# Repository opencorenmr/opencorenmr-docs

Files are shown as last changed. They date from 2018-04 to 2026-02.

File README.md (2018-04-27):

## Welcome to GitHub Pages

You can use the [editor on GitHub](https://github.com/opencorenmr/opencorenmr.github.io/edit/master/README.md) to maintain and preview the content for your website in Markdown files.

Whenever you commit to this repository, GitHub Pages will run [Jekyll](https://jekyllrb.com/) to rebuild the pages in your site, from the content in your Markdown files.

### Markdown

Markdown is a lightweight and easy-to-use syntax for styling your writing. It includes conventions for

```markdown
Syntax highlighted code block

# Header 1
## Header 2
### Header 3

- Bulleted
- List

1. Numbered
2. List

**Bold** and _Italic_ and `Code` text

[Link](url) and ![Image](src)
```

For more details see [GitHub Flavored Markdown](https://guides.github.com/features/mastering-markdown/).

### Jekyll Themes

Your Pages site will use the layout and styles from the Jekyll theme you have selected in your [repository settings](https://github.com/opencorenmr/opencorenmr.github.io/settings). The name of this theme is saved in the Jekyll `_config.yml` configuration file.

### Support or Contact

Having trouble with Pages? Check out our [documentation](https://help.github.com/categories/github-pages-basics/) or [contact support](https://github.com/contact) and we’ll help you sort it out.

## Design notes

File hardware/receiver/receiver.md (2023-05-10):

# Receiver

11 Mar 2019 Revised by Kazuyuki Takeda
8 Mar 2019 document created by Kazuyuki Takeda

[Back to Home](../../index.md)  

- - -
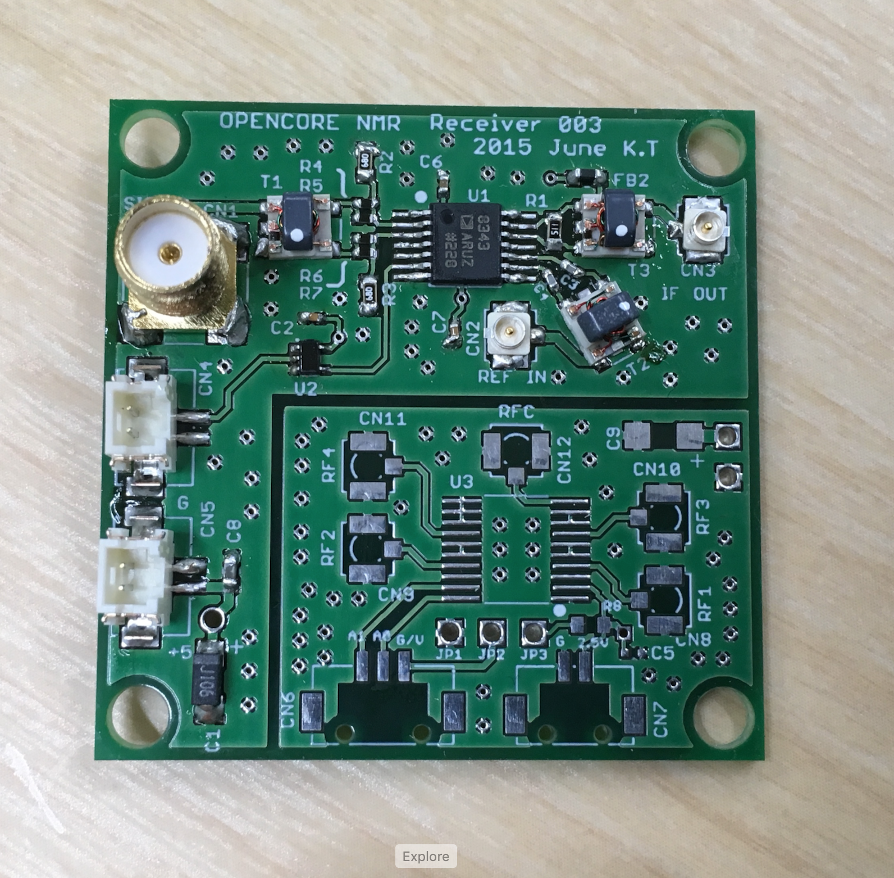
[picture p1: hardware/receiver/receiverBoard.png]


Note that the right bottom part of the board serves for an optional receiver-channel selector. That is, you may leave this part blank, like the one in the photo shown here. In our lab we make fully use of it. How to built/use the channel selector will be described elsewhere.

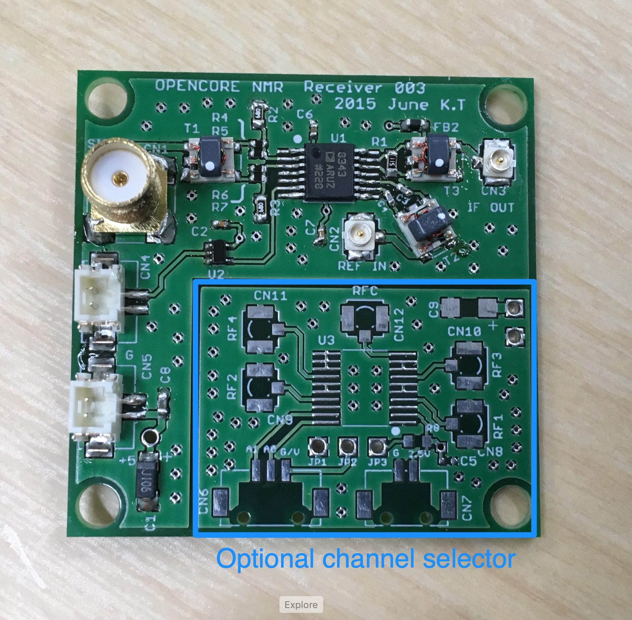
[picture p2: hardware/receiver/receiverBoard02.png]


### Board Design  

- The board was designed on EAGLE 6.2.0 Professional  
- There are **4 layers**. That is, in addition to the top and bottom layers, the board has two inner layers.  

##### EAGLE schematic and board files
- Schematic: [rcvr003.sch](data/rcvr003.sch)  
- Board: [rcvr003.brd](data/rcvr003.brd)  

##### Gerber files

- [rcvr003.cmp](data/gerber/rcvr003.cmp) (Component side pattern)
- [rcvr003.plc](data/gerber/rcvr003.plc)（Component side silkscreen)
- [rcvr003.sol](data/gerber/rcvr003.sol)（Solder side pattern）
- [rcvr003.stc](data/gerber/rcvr003.stc)（Component side solder resist）
- [rcvr003.sts](data/gerber/rcvr003.sts)（Solder side solder resist）
- [rcvr003.2l](data/gerber/rcvr003.2l)（2nd (inner) layer pattern）
- [rcvr003.3l](data/gerber/rcvr003.3l)（3rd (inner) layer pattern）
- [rcvr003.out](data/gerber/rcvr003.out)（outline）
- [rcvr003.dri](data/gerber/rcvr003.dri) (drill list）
- [rcvr003.drd](data/gerber/rcvr003.drd)（drill data）

**Note**: The *component side* mean the top (1st) layer, while the *solder side* does the bottom layer.

##### Component layer
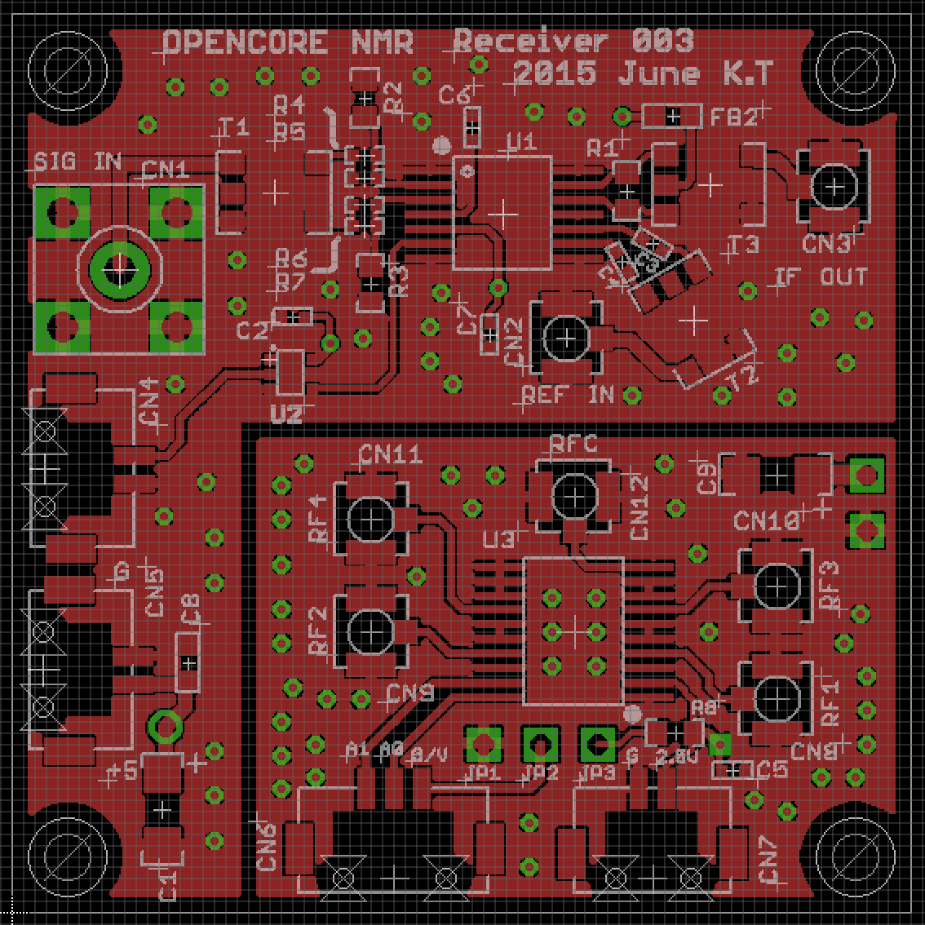
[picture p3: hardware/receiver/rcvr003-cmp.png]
  

##### 2nd (inner) layer
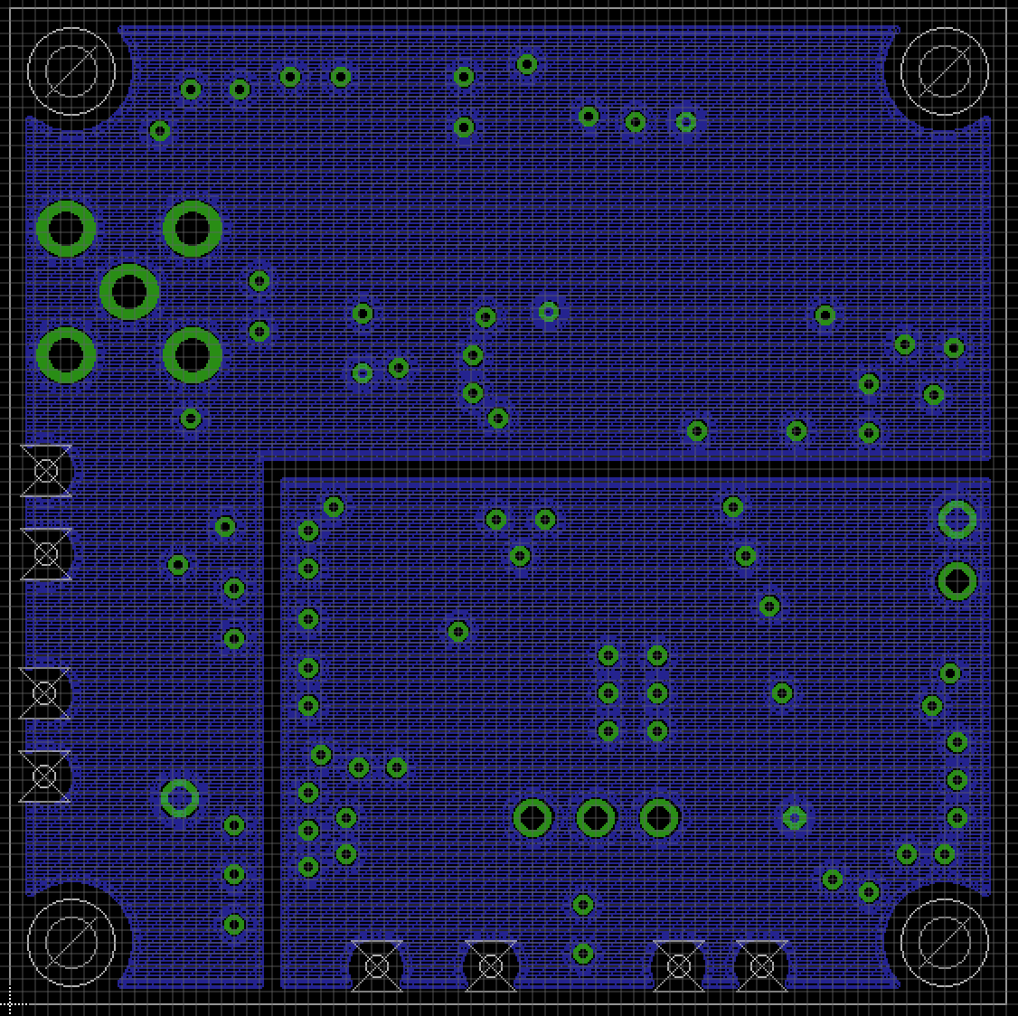
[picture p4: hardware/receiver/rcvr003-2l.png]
  

##### 3rd (inner) layer
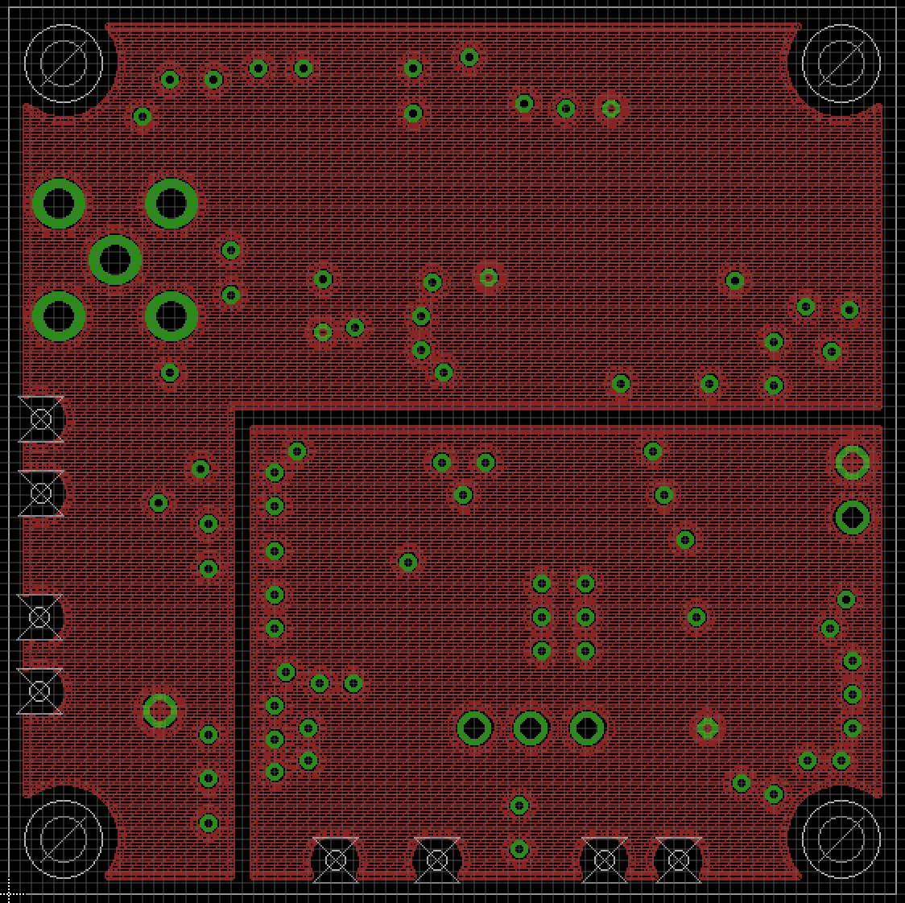
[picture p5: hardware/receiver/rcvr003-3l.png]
  

##### Bottom layer
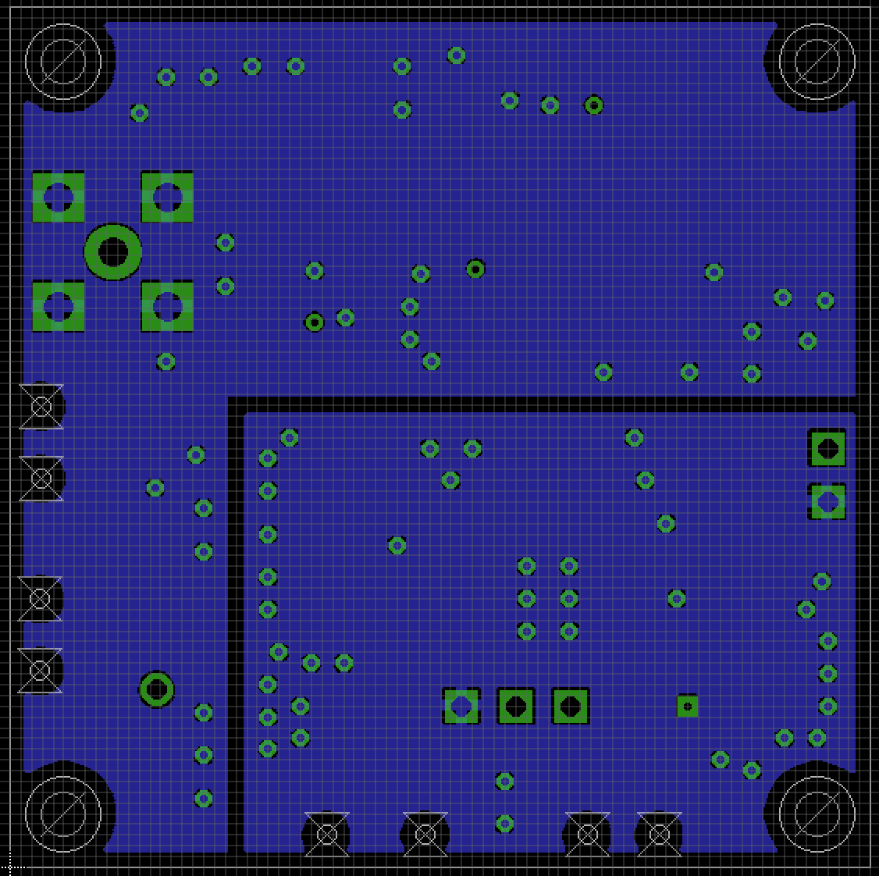
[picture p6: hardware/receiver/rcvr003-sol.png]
  

### Parts List

Part| 	Value | 	Device | 	Package	| Description
---|---|---|---|---
C1  | 10u	  | Tantalum Capacitor |3216 (polar) 	|
C2  | 0.01u	| Capacitor	| 1005	|
C3  | 0.1u	| Capacitor	| 1005	|
C4  | 0.1u	| Capacitor	| 1005	|
C5  | 0.1u	| Capacitor	| 1005	|
C6  | 0.1u	| Capacitor	| 1005	|
C7  | 0.01u	| Capacitor	| 1005	|
C8  | 0.01u	| Capacitor	| 1608	|
C9  | 10u	  | Tantalum Capacitor | 3216 (polar)	|
CN1 | |  SMA Straight PCB Socket | | 5-1814832-1 (TE Connectivity)
CN2 | |  U.FL-R-SMT |		| HIROSE
CN3 | |  U.FL-R-SMT | 	| HIROSE
CN4 | |  DF13-2P-1.25V	| 1.25mm Pitch Miniature Crimping Connector | HIROSE
CN5 | |  DF13-2P-1.25V	| 1.25mm Pitch Miniature Crimping Connector | HIROSE		
CN6 | |  DF13-3P-1.25V	| 1.25mm Pitch Miniature Crimping Connector | HIROSE		
CN7 | |  DF13-2P-1.25V	| 1.25mm Pitch Miniature Crimping Connector | HIROSE		
CN8 | |  U.FL-R-SMT |		| HIROSE
CN9 | |  U.FL-R-SMT |		| HIROSE
CN10|	|  U.FL-R-SMT |		| HIROSE
CN11|	|  U.FL-R-SMT |		| HIROSE
CN12|	|  U.FL-R-SMT |		| HIROSE
FB2  |  30 Ohm @ 100 MHz   |  MPZ1608S300A   | 1608   | Ferrite bead (TDK)    
R1  |	  510 | Resistor	| 1608
R2  |	  68  | Resistor	| 1608
R3  |	  68  | Resistor	| 1608
R4  |	  10  | Resistor	| 1005
R5  |	  10  | Resistor	| 1005
R6  |	  10  | Resistor	| 1005
R7  |	  10  | Resistor	| 1005
R8  |	  100 |  Resistor	| 1608
T1  |	  | TC4-1W+	   |  AT224	| RF transformer (Mini Circuits)
T2  |	  | TC1-1-13M+ | 	AT224	| RF transformer (Mini Circuits)
T3  |	  | TC4-1W+    | 	AT224	| RF transformer (Mini Circuits)
U1  |	  | AD8343     | 		
U2  |	  | MC74VHC1G04| 	 | Logic Inverter
U3  |	  | ADG904     | 	TSSOP

- - -
[Back to Top](../../index.md)

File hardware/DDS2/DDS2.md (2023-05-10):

# DDS2

9 Mar 2019 Revised by Kazuyuki Takeda
2 Mar 2019 Kazuyuki Takeda

[Back to Home](../../index.md)  
- - -

This board serves for a direct digital synthesizer (DDS). Each rf channel of the Opencore NMR spectrometer is equipped with two separate DDS. The first DDS is implemented on the [mother board](../motherBoard/motherMoard.md). Here, we described the *second* one, which we call DDS2.
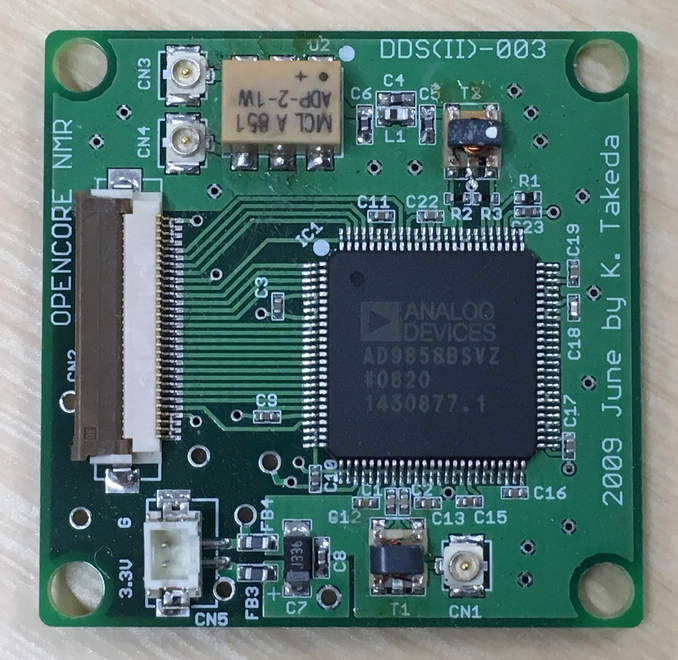
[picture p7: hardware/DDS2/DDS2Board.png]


- - -

### Board design

- The board was designed on EAGLE 6.2.0 Professional  
- There are **4 layers**. That is, in addition to the top and bottom layers, the board has two inner layers.  

##### EAGLE schematic and board files
- Schematic: [DDS2-03.sch](data/DDS2-03.sch)  
- Board: [DDS2-03.brd](data/DDS2-03.brd)  

##### Gerber files
- [DDS2-03.cmp](data/gerber/DDS2-03.cmp)  (Component side pattern)
- [DDS2-03.plc](data/gerber/DDS2-03.plc)  (Component side silkscreen)
- [DDS2-03.sol](data/gerber/DDS2-03.sol)  (Solder side pattern)
- [DDS2-03.stc](data/gerber/DDS2-03.stc)  (Component side solder resist)
- [DDS2-03.sts](data/gerber/DDS2-03.sts)  (Solder side solder resist)
- [DDS2-03.pls](data/gerber/DDS2-03.pls)  (Solder side silkscreen)
- [DDS2-03.2l ](data/gerber/DDS2-03.2l )  (2nd (inner) layer pattern)
- [DDS2-03.3l ](data/gerber/DDS2-03.3l )  (3rd (inner) layer pattern)
- [DDS2-03.out](data/gerber/DDS2-03.out)  (outline)
- [DDS2-03.dri](data/gerber/DDS2-03.dri)  (drill list)
- [DDS2-03.drd](data/gerber/DDS2-03.drd)  (drill data)

**Note**: The *component side* mean the top (1st) layer, while the *solder side* does the bottom layer.

##### Component side (1st layer)
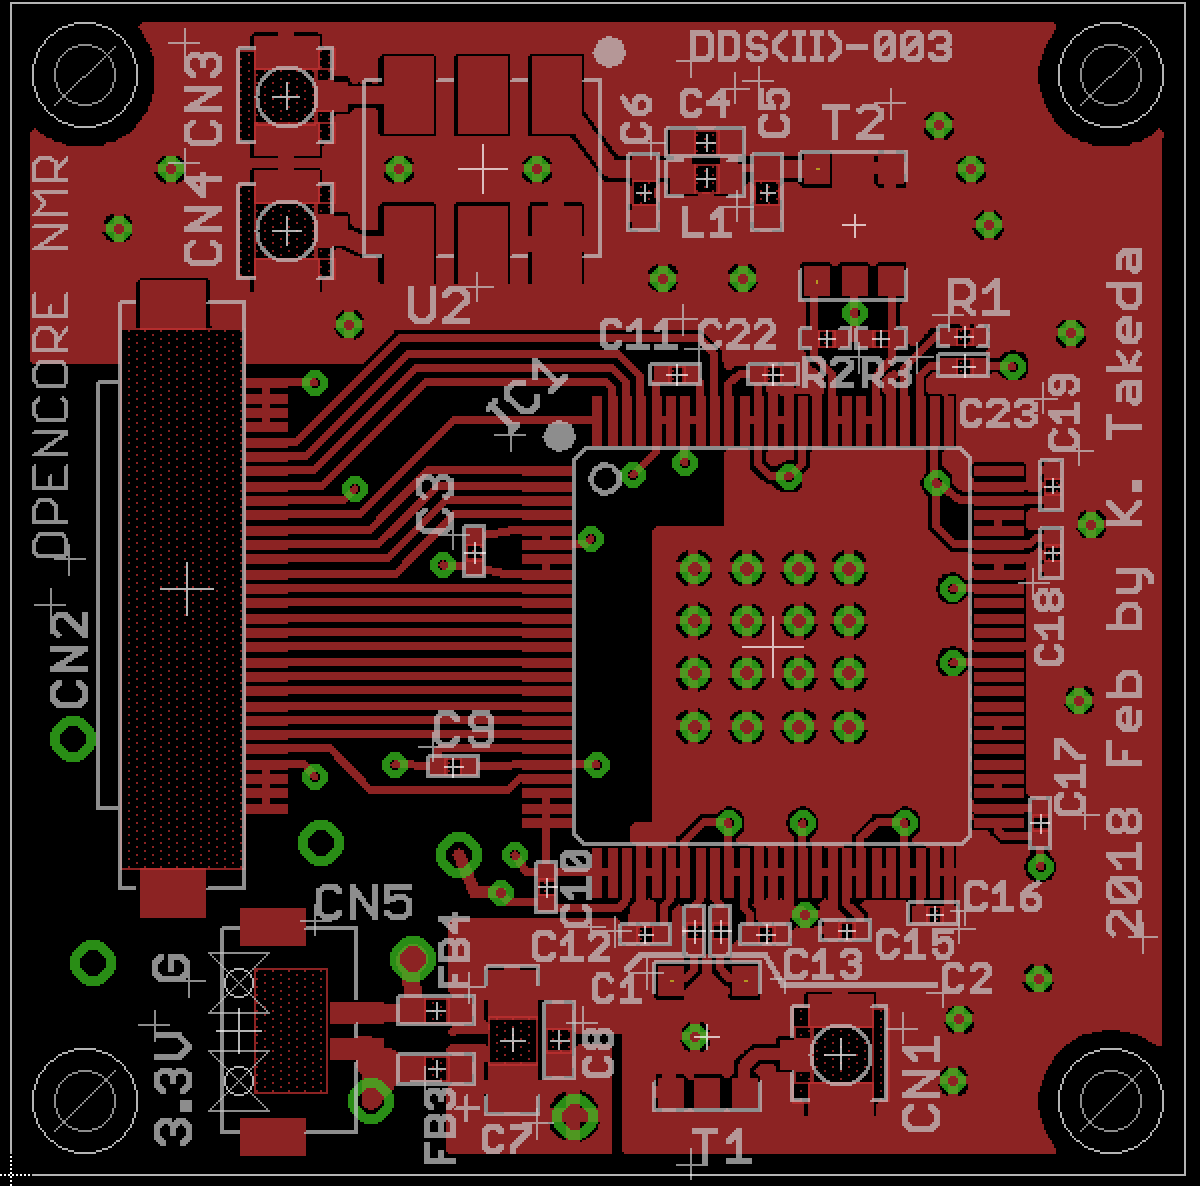
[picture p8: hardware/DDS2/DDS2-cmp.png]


##### 2nd (inner) layer
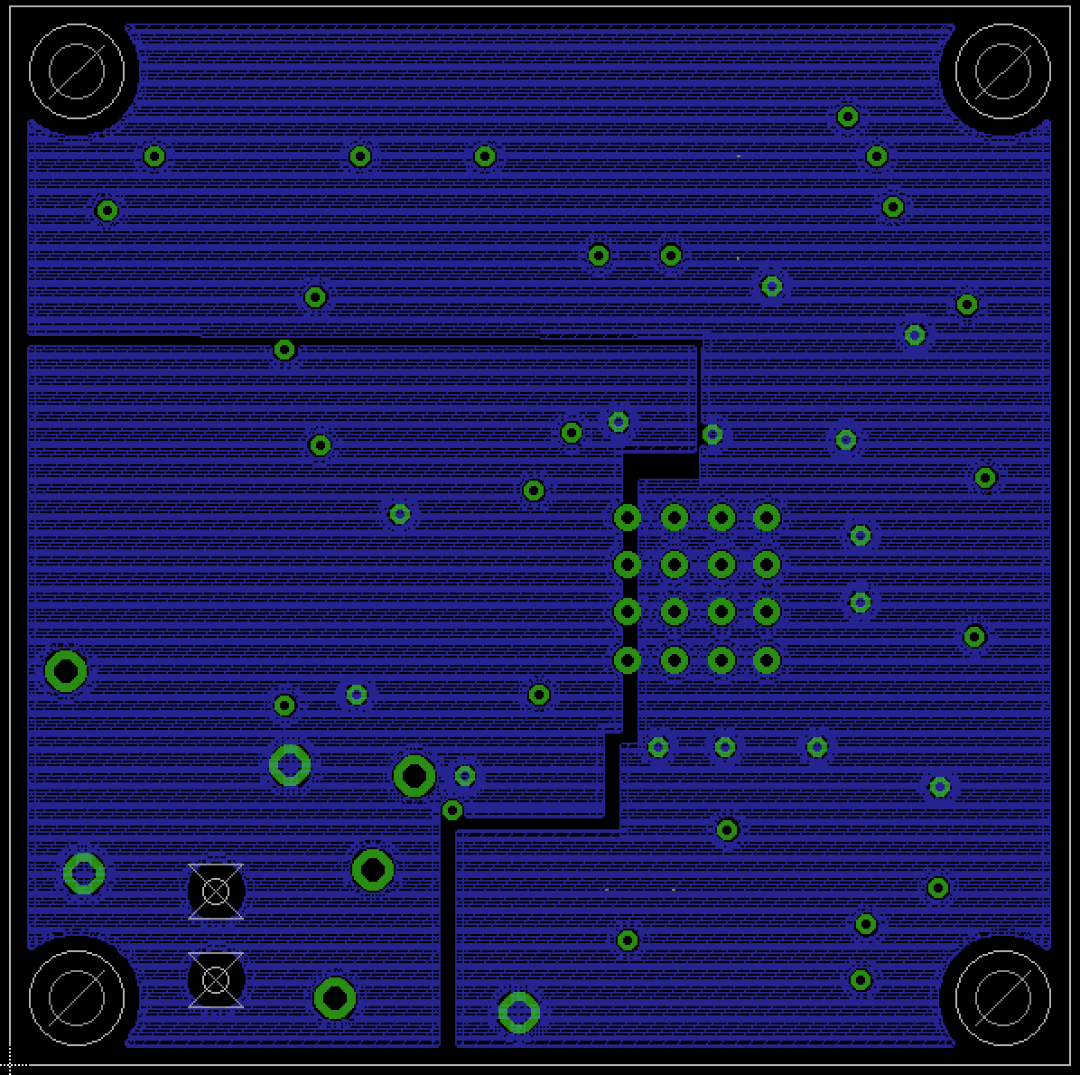
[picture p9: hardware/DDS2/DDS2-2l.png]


##### 3rd (inner) layer
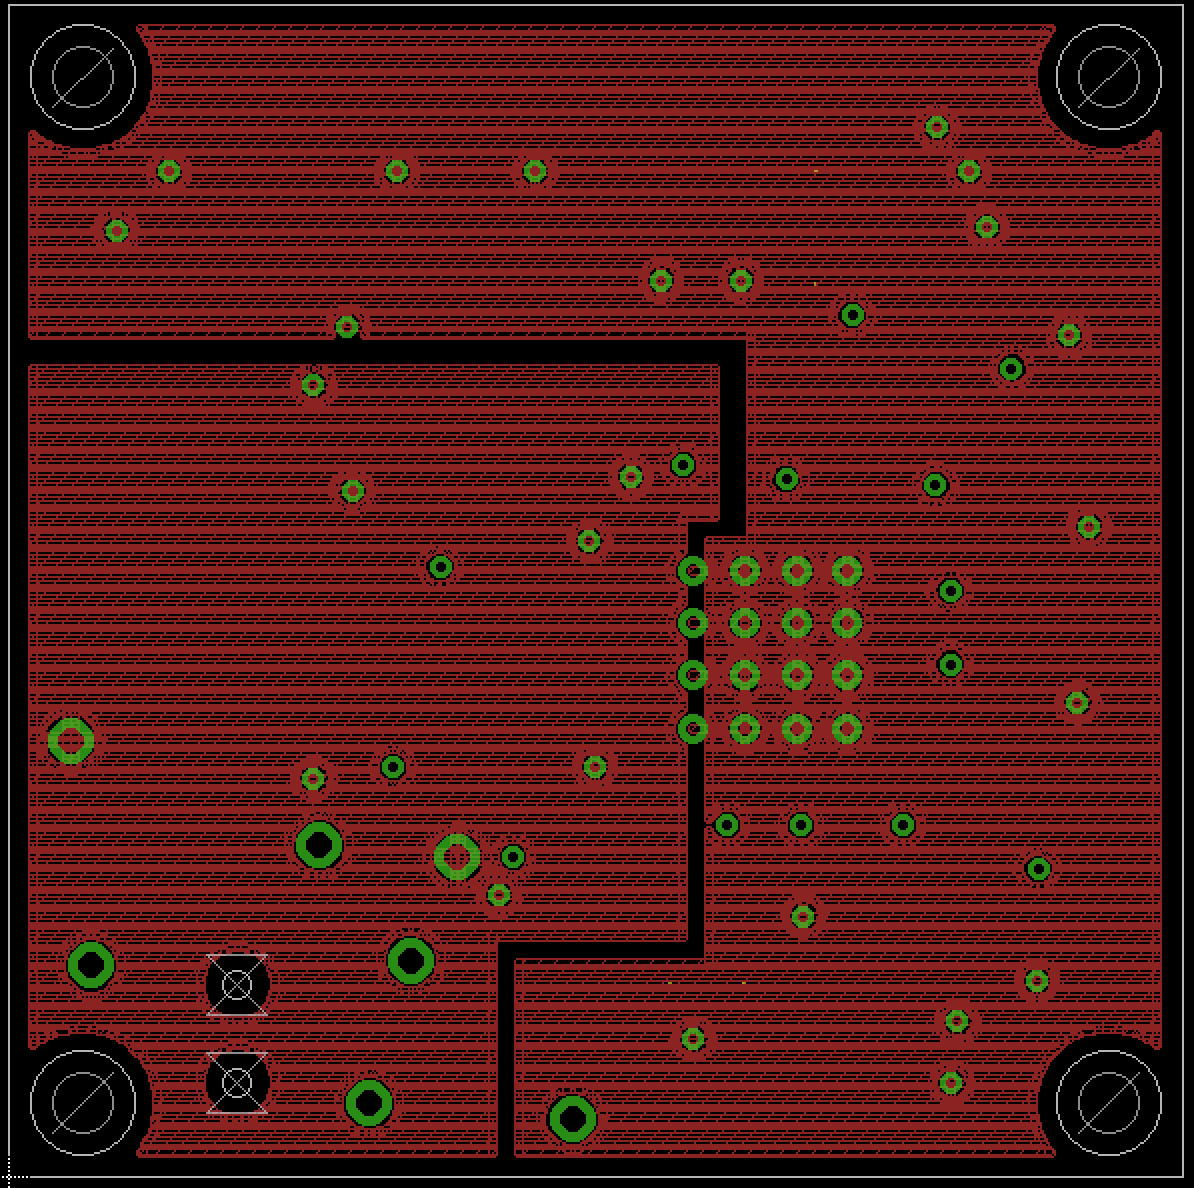
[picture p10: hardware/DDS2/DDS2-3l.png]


##### Solder side (bottom layer)
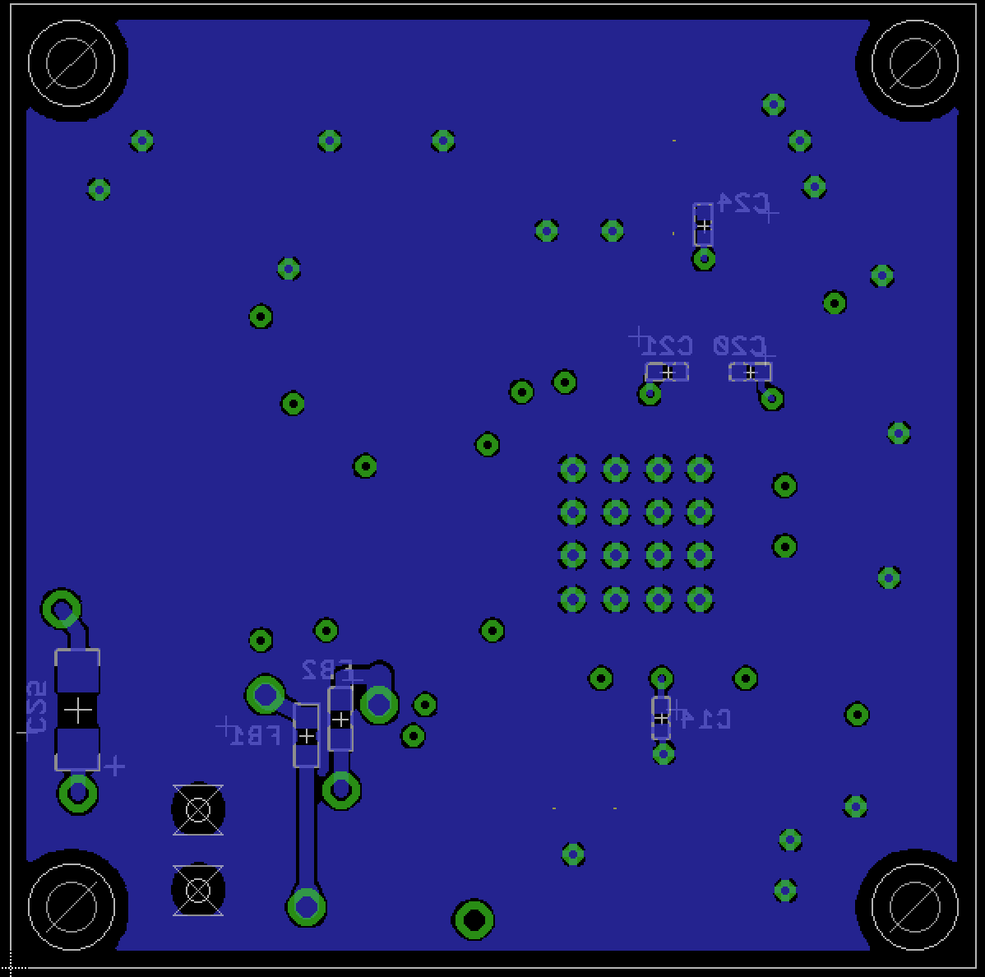
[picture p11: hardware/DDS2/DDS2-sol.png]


### Parts List

Part	| Value | 	Device	| Package | Description
---|---|---|---|---
C1	| 1000p	| C	| 1005
C2	| 1000p	| C	| 1005
C3	| 0.1u	| C	| 1005
C4	| 6p	  | C	| 1608
C5	| 12p	  | C	| 1608
C6	| 12p	  | C	| 1608
C7	| 33u	  | C	| 3216 (polar) | tantalum
C8	| 0.01u	| C	| 1608
C9	| 0.1u	| C	| 1005
C10	| 0.1u	| C	| 1005
C11	| 0.1u	| C	| 1005
C12	| 0.01u	| C	| 1005
C13	| 0.01u	| C	| 1005
C14	| 0.01u	| C	| 1005
C15	| 0.01u	| C	| 1005
C16	| 0.01u	| C	| 1005
C17	| 0.01u	| C	| 1005
C18	| 0.01u	| C	| 1005
C19	| 0.01u	| C	| 1005
C20	| 0.01u	| C	| 1005
C21	| 0.01u	| C	| 1005
C22	| 0.01u	| C	| 1005
C23	| 0.1u	| C	| 1005
C24	| 0.01u	| C	| 1005
C25	| 33u	  | C	| 3216 (polar) | tantalum
CN1	| 	    | U.FL-R-SMT | | (HIROSE)		
CN2	| 	    | FH12-30S-0.5SH | | (HIROSE)		0.5mm pitch FPC connector
CN3	| 	    | U.FL-R-SMT | | (HIROSE)		
CN4	| 	    | U.FL-R-SMT | | (HIROSE)		
CN5	| 	    | DF13-2P-1.25V | | (HIROSE)		
FB1  |  30 Ohm @ 100 MHz   |  MPZ1608S300A   | 1608           | Ferrite bead (TDK)
FB2  |  30 Ohm @ 100 MHz   |  MPZ1608S300A   | 1608           | Ferrite bead (TDK)
FB3  |  30 Ohm @ 100 MHz   |  MPZ1608S300A   | 1608           | Ferrite bead (TDK)
FB4  |  30 Ohm @ 100 MHz   |  MPZ1608S300A   | 1608           | Ferrite bead (TDK)
U1	| 	    | AD9858 | | (Analog Divices)		DDS chip
L1	| 12nH	| L | 1608
R1	| 2k	  | R | 1005
R2	| 27	  | R | 1005
R3	| 27	  | R | 1005
T1	| 	    | TC1-1-13M+ | | (Mini Circuits)	AT224	RF transformer
T2	| 	    | TC1-1T+ |  |(Mini Circuits)	AT224	RF transformer
U2	| 	    | ADP-2-1W | | (Mini Circuits)		RF splitter

- - -
[Back to Home](../../index.md)

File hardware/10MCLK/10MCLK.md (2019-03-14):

# 10 MHz Clock

14 Mar 2019 Kazuyuki Takeda

[Back to Home](../../index.md)  
- - -

This board generates a clock signal at 10 MHz. On the board, the clock signal is fan-out into several ports. The 10 MHz clock signal is required for the [mother board](../motherBoard/motherMoard.md). as well as 1 GHz clock module, to be described in due time.
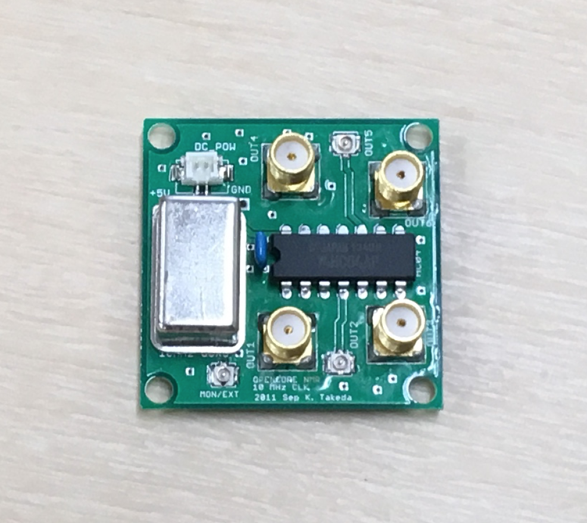
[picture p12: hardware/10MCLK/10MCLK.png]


- - -

### Board design

- The board was designed on EAGLE 6.2.0 Professional  
- There are **2 layers**, the top and the bottom layers.

##### EAGLE schematic and board files
- Board: [10MCLK02.brd](data/10MCLK02.brd)  

##### Gerber files
- [10MCLK02.cmp](data/gerber/10MCLK02.cmp)  (Component side pattern)
- [10MCLK02.plc](data/gerber/10MCLK02.plc)  (Component side silkscreen)
- [10MCLK02.sol](data/gerber/10MCLK02.sol)  (Solder side pattern)
- [10MCLK02.stc](data/gerber/10MCLK02.stc)  (Component side solder resist)
- [10MCLK02.sts](data/gerber/10MCLK02.sts)  (Solder side solder resist)
- [10MCLK02.out](data/gerber/10MCLK02.out)  (outline)
- [10MCLK02.dri](data/gerber/10MCLK02.dri)  (drill list)
- [10MCLK02.drd](data/gerber/10MCLK02.drd)  (drill data)

**Note**: The *component side* mean the top (1st) layer, while the *solder side* does the bottom layer.

##### Component side (1st layer)
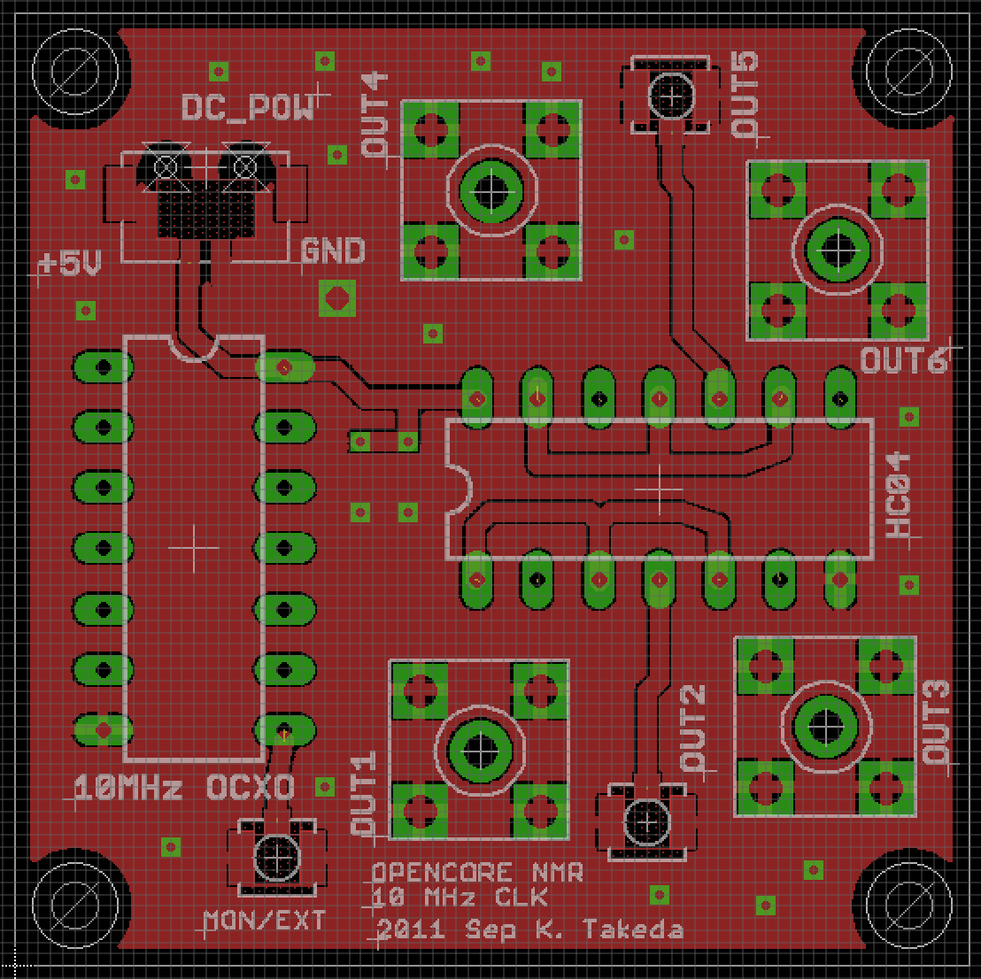
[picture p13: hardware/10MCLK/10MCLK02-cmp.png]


##### Solder side (bottom layer)
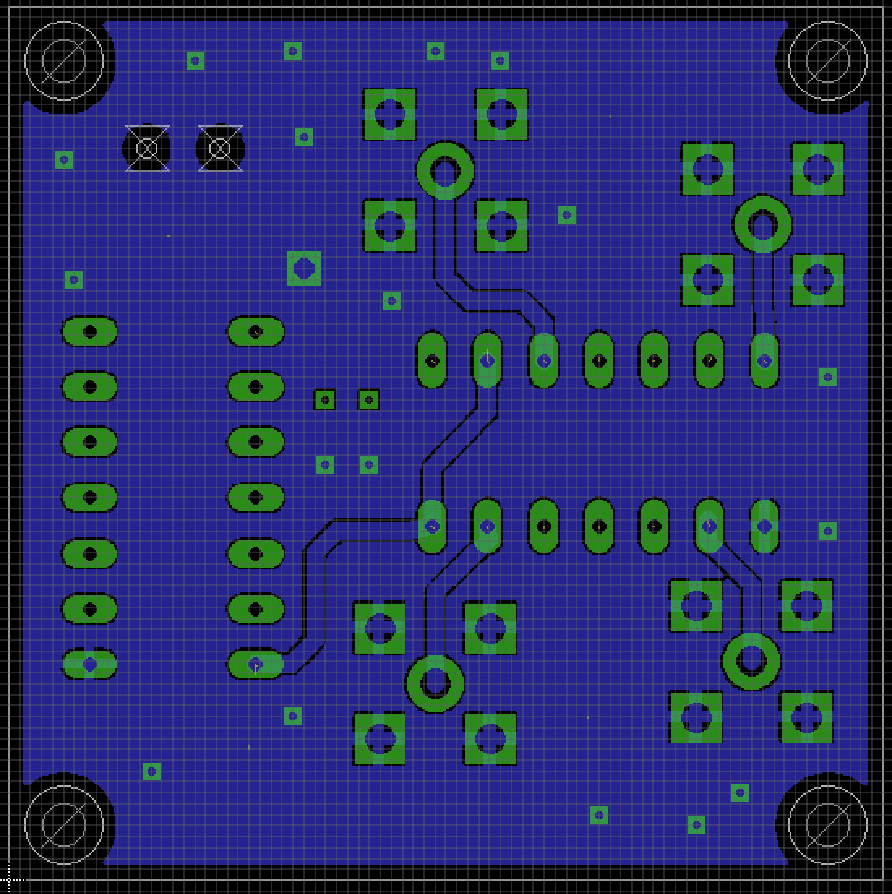
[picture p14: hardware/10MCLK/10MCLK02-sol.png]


### Parts List (TODO)

Part	| Value | 	Device	| Package | Description
---|---|---|---|---
CN	| 	    | U.FL-R-SMT | | (HIROSE)		
CN	| 	    | U.FL-R-SMT | | (HIROSE)		
CN	| 	    | U.FL-R-SMT | | (HIROSE)		

CN	 | 	    | DF13-2P-1.25V | | (HIROSE) 		
CN | |  SMA Straight PCB Socket | | 5-1814832-1 (TE Connectivity)
CN | |  SMA Straight PCB Socket | | 5-1814832-1 (TE Connectivity)
CN | |  SMA Straight PCB Socket | | 5-1814832-1 (TE Connectivity)
CN | |  SMA Straight PCB Socket | | 5-1814832-1 (TE Connectivity)
OCXO   |  | MOFH5200C-10.000 |  | (MMD)
IC  |  | HC04 |
- - -
[Back to Home](../../index.md)

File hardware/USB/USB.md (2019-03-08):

# USB board

5 Mar 2019 Kazuyuki Takeda

[Back to Home](../../index.md)  

- - -
  

This is a 40x40 mm board equipped with FT2232, a dual-line USB driver by [FTDI](https://www.ftdichip.com) inc. This enables apparent simultaneous two-channel data communication between the OPENCORE NMR spectrometer and the console software installed on a personal computer through a single USB cable. In the current architecture of the OPENCORE NMR, the one channel (channel A) is used in the UART 232 mode for sending/receiving the commands/responses to/from the PPG interface core module built inside the FPGA chip, the other (channel B) for transferring the NMR signals from the RCVR core module to the personal computer in the 245 FIFO mode.

Before using, the mode of operation must be configured to the EPROM on the board using the [MProg](https://www.ftdichip.com/Support/Utilities.htm#MProg) software (FTDI).
- [A document on EPROM configuration](https://github.com/opencorenmr/opencorenmr-docs/blob/master/blog/usb_eprom/mprog.md)  

Also, the [D2XX driver](https://www.ftdichip.com/Drivers/D2XX.htm), which is available from FTDI, has to be installed.  

### Board design

- The board was designed on EAGLE 6.2.0 Professional  
- There are **2 layers**, namely, the top (component) and bottom (solder) layers.

##### EAGLE schematic and board files
- Schematic: [USB.sch](data/USB.sch)  
- Board: [USB.brd](data/USB.brd)  

##### Gerber files

- [USB.cmp](data/gerber/USB.cmp) (Component side pattern)
- [USB.plc](data/gerber/USB.plc)（Component side silkscreen)
- [USB.sol](data/gerber/USB.sol)（Solder side pattern）
- [USB.stc](data/gerber/USB.stc)（Component side solder resist）
- [USB.sts](data/gerber/USB.sts)（Solder side solder resist）
- [USB.pls](data/gerber/USB.pls)（Solder side silkscreen）
- [USB.out](data/gerber/USB.out)（outline）
- [USB.dri](data/gerber/USB.dri) (drill list）
- [USB.drd](data/gerber/USB.drd)（drill data）

**Note**: The *component side* mean the top (1st) layer, while the *solder side* does the bottom layer.

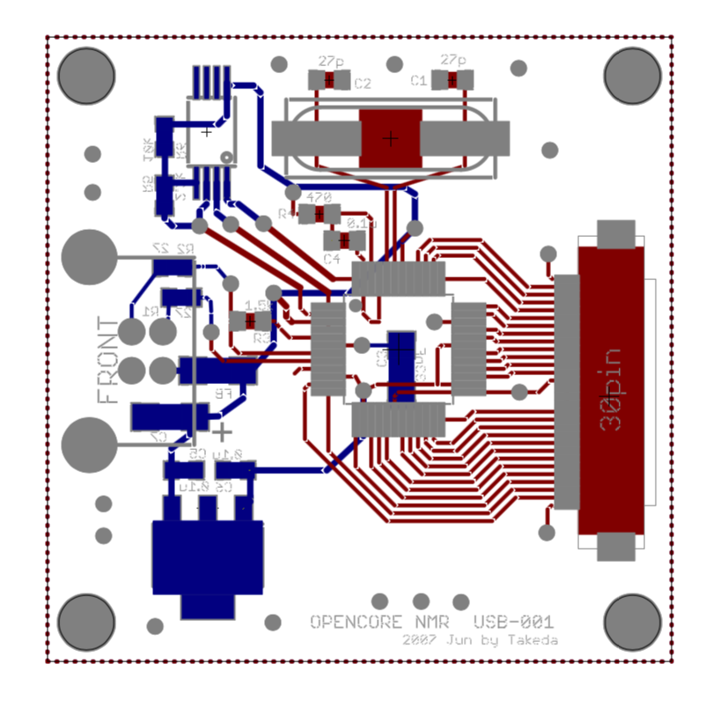
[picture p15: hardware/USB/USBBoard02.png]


### Parts List

Part  | Value  | Device  | Package  | Description
--|---|---|---|--
C1	| *27p | 	C |	1608 |
C2	| *27p | 	C |	1608 |
C3	| 33nF | 	C |	3216 |
C4	| 0.1u | 	C |	1608 |
C5	| 0.1u | 	C |	1608 |
C6	| 0.1u | 	C |	1608 |
C7	| 10u  | 	C |	3216 (polar) | tantalum
CN1	|  | FH12-30S-0.5SH 	| | 	0.5 mm pitch FPC connector (HIROSE)
FB  |  30 Ohm @ 100 MHz   |  MPZ1608S300A   | 1608           | Ferrite bead (TDK)
R1	| 27	  | R	| 1608	|
R2	| 27	  | R	| 1608	|
R3	| 1.5k	| R	| 1608	|
R4	| 470	  | R	| 1608	|
R5	| 2.2k	| R	| 1608	|
R6	| 10k	  | R	| 1608	|
U1	|  | FT2232D	|	| Dual USB UART/FIFO I.C. (FTDI)
U2	|  | 67068-704J  |	|	USB connector (MOLEX)
U3	|  | **AT93C46-10TU-2.7	|  Thin Shrink Small Outline Package (TSSOP) |	Serial EPROM (ATMEL)
U4	|  | LM2937IMP-3.3	| SOT-223	| Voltage regulator
Y1	| 6 MHz	| HC49/4H SMX	| |	6 MHz crystal

*Note: The proper value for C1 and C2 depends on the crystal oscillator. Check the datasheet of the 6 MHz crystal that you use.

**Note: End of production. There should be alternatives. According to the datasheet of FT2232D, EEPROMs with a 16-bit wide configuration are required. And the EEPROM must be operational at a 1 MHz clock rate with a supply voltage between 4.35V and 5.25V.

- - -
[Back to Home](../../index.md)

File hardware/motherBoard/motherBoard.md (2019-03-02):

# Mother board

23 Feb 2019 Kazuyuki Takeda

[Back to Home](../../index.md)  

- - -

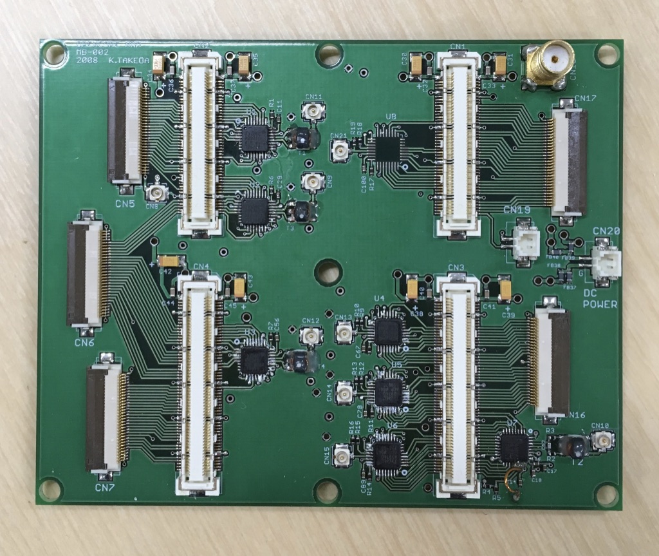
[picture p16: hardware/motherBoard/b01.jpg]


This board, called the *mother board*, is to be docked by either of the following commercial FPGA breadboards:
- [ACM-202-80C8](https://www2.hdl.co.jp/en/altera-series1/cycloneiii/acm-202-ql.html)  (HuMANDATA LTD.)  
- [ACM-206-A7](https://www2.hdl.co.jp/en/altera-series1/cyclonev/acm-206-ql.html) (HuMANDATA LTD.)  



The photo just below shows the *docked* board:
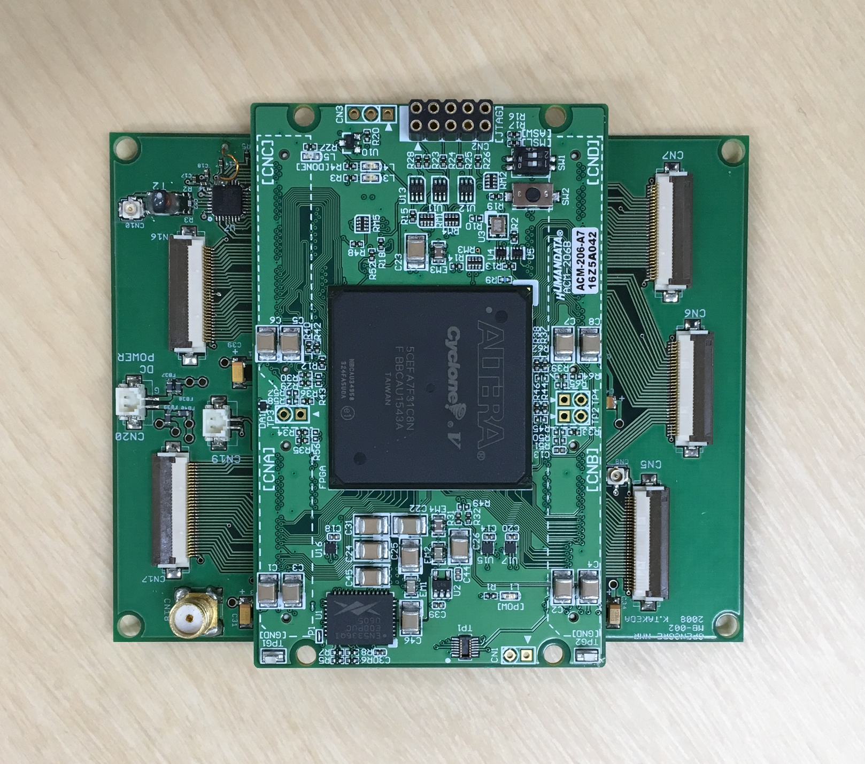
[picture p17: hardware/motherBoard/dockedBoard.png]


- - -

### Board design

- The board was designed on EAGLE 6.2.0 Professional  
- There are **4 layers**. That is, in addition to the top and bottom layers, the board has two inner layers.  

##### EAGLE schematic and board files
- Schematic: [mother-002.sch](data/mother-002.sch)  
- Board: [mother-002.brd](data/mother-002.brd)  

##### Gerber files

- [mother-002.cmp](data/gerber/mother-002.cmp) (Component side pattern)
- [mother-002.plc](data/gerber/mother-002.plc)（Component side silkscreen)
- [mother-002.sol](data/gerber/mother-002.sol)（Solder side pattern）
- [mother-002.stc](data/gerber/mother-002.stc)（Component side solder resist）
- [mother-002.sts](data/gerber/mother-002.sts)（Solder side solder resist）
- [mother-002.pls](data/gerber/mother-002.pls)（Solder side silkscreen）
- [mother-002.2l](data/gerber/mother-002.2l)（2nd (inner) layer pattern）
- [mother-002.3l](data/gerber/mother-002.3l)（3rd (inner) layer pattern）
- [mother-002.out](data/gerber/mother-002.out)（outline）
- [mother-002.dri](data/gerber/mother-002.dri) (drill list）
- [mother-002.drd](data/gerber/mother-002.drd)（drill data）

**Note**: The *component side* mean the top (1st) layer, while the *solder side* does the bottom layer.

##### Component side (1st layer)
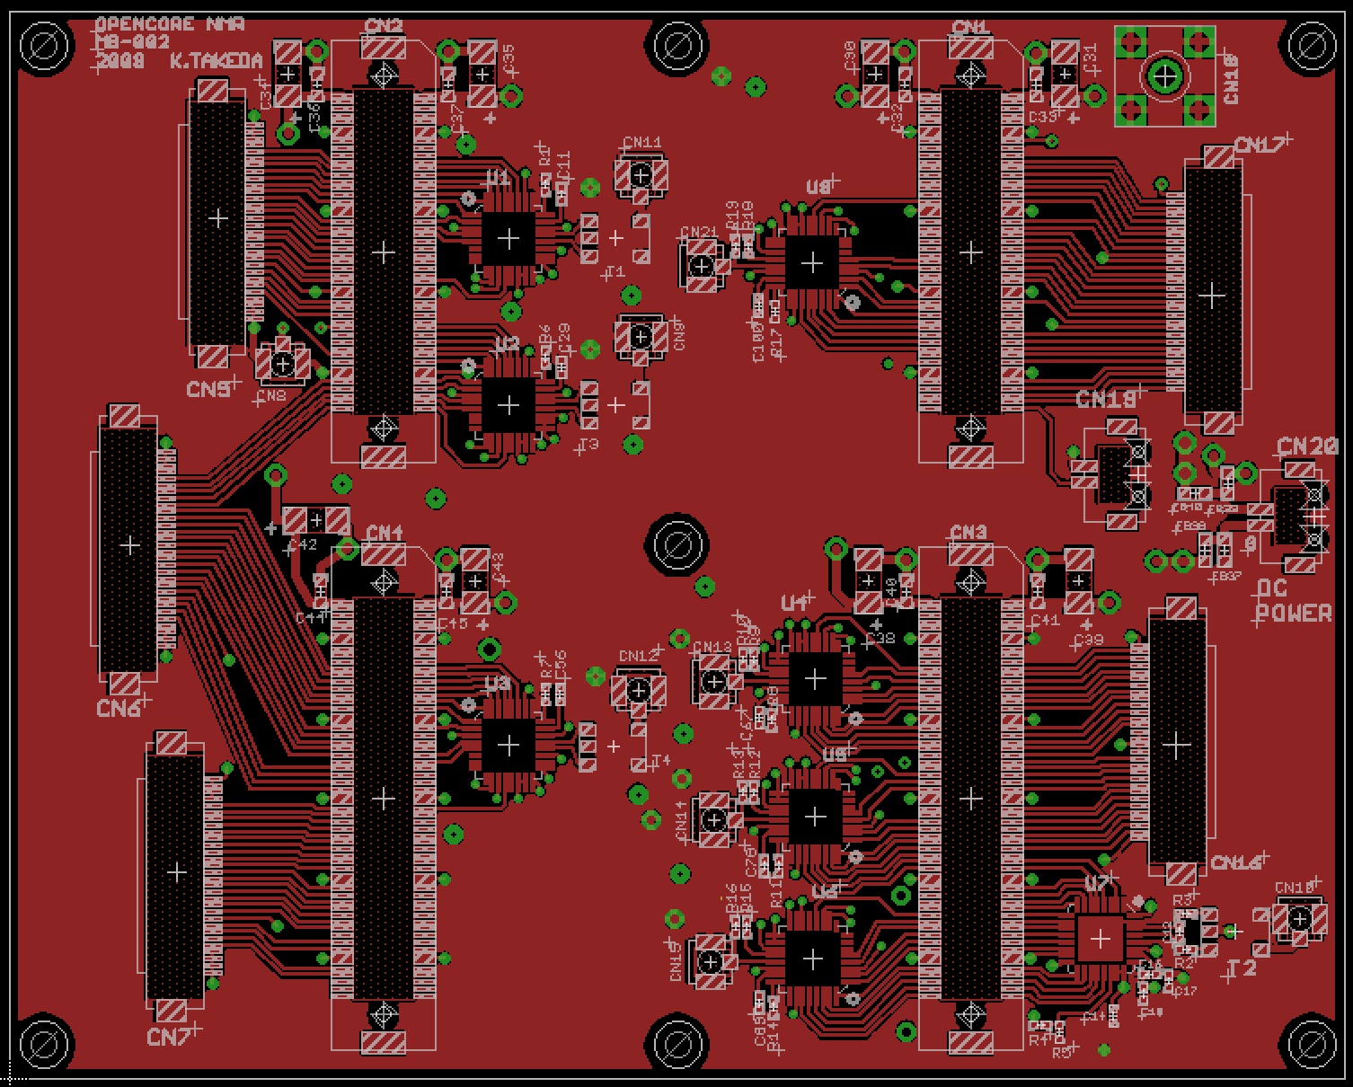
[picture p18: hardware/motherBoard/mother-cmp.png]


##### 2nd (inner) layer
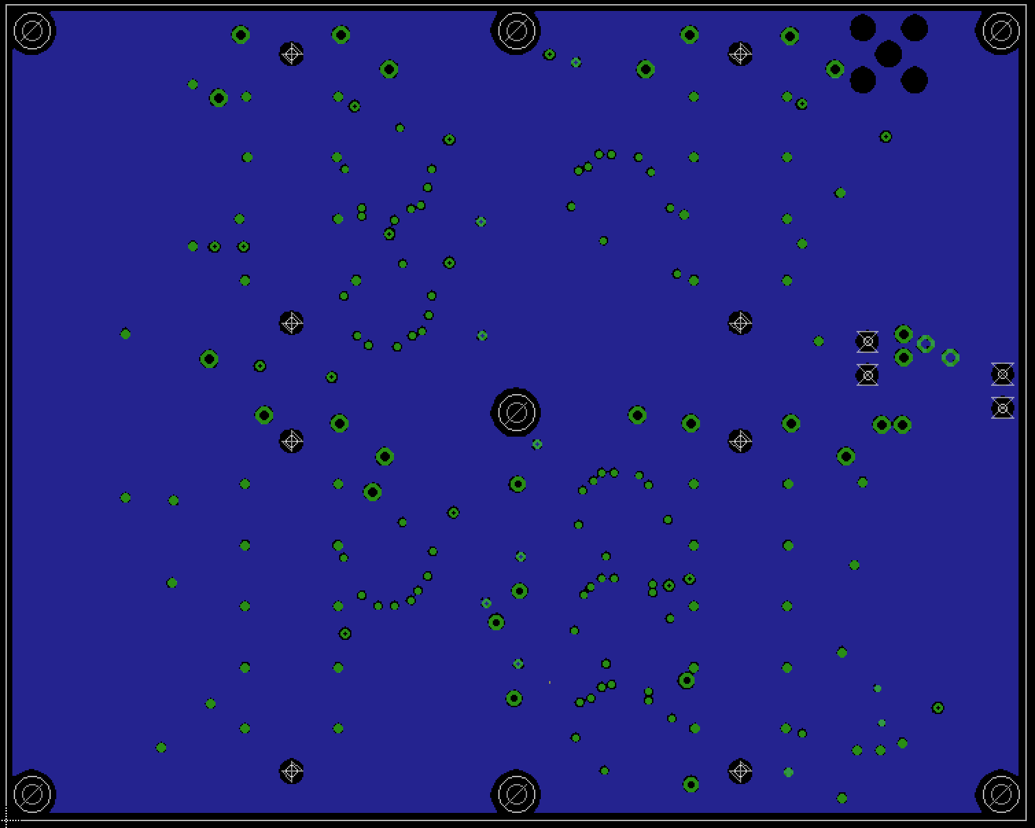
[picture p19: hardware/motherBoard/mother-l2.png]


##### 3rd (inner) layer
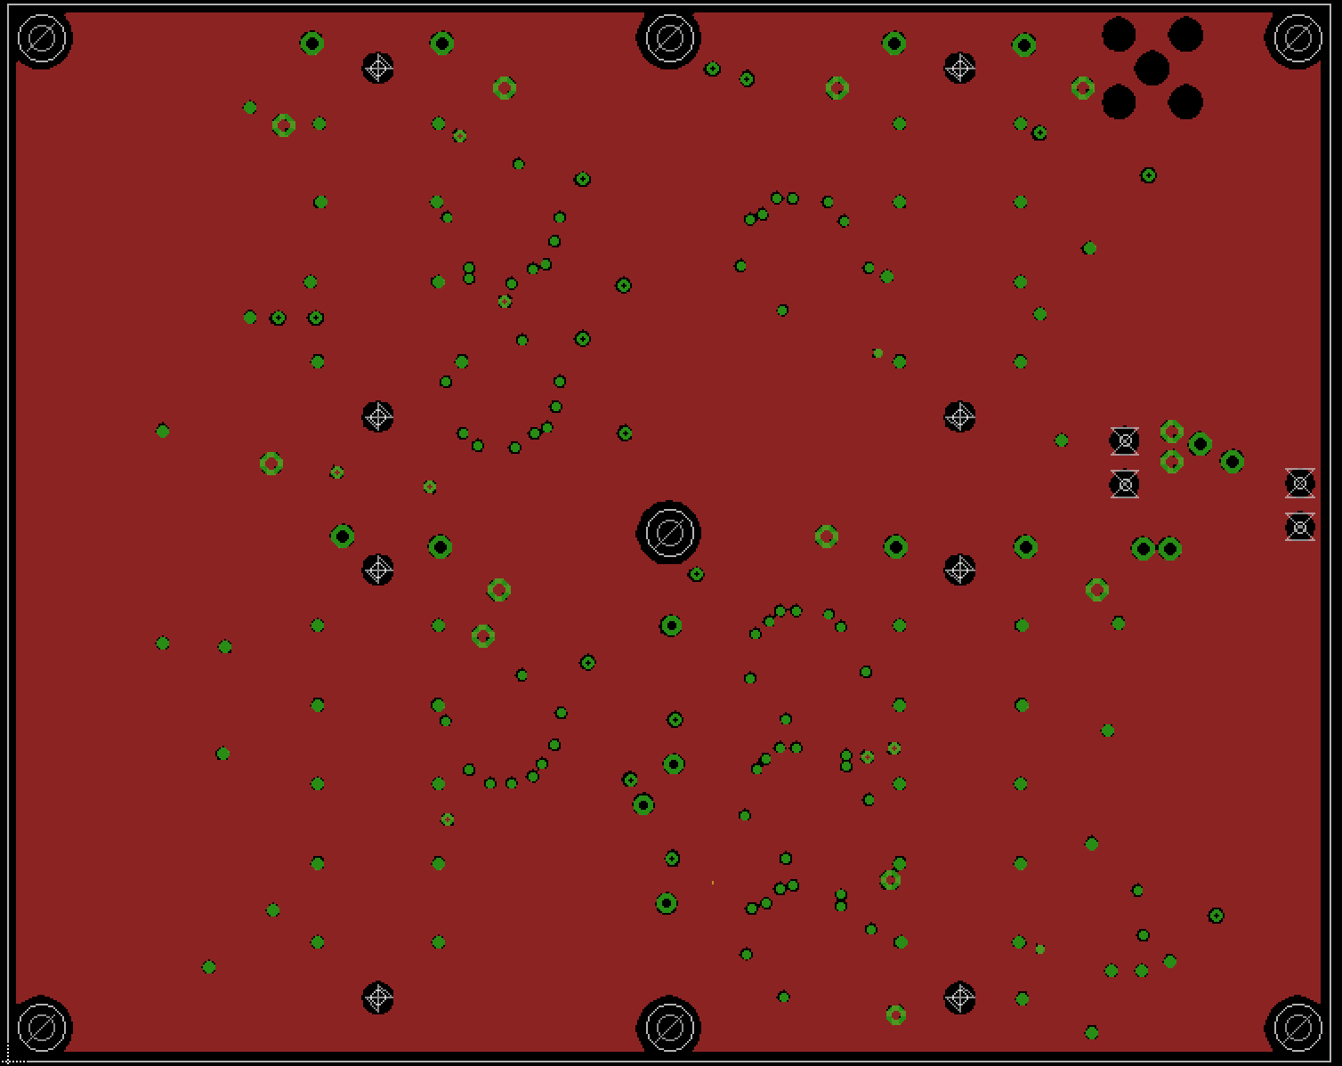
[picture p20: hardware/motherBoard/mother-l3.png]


##### Solder side (bottom layer)
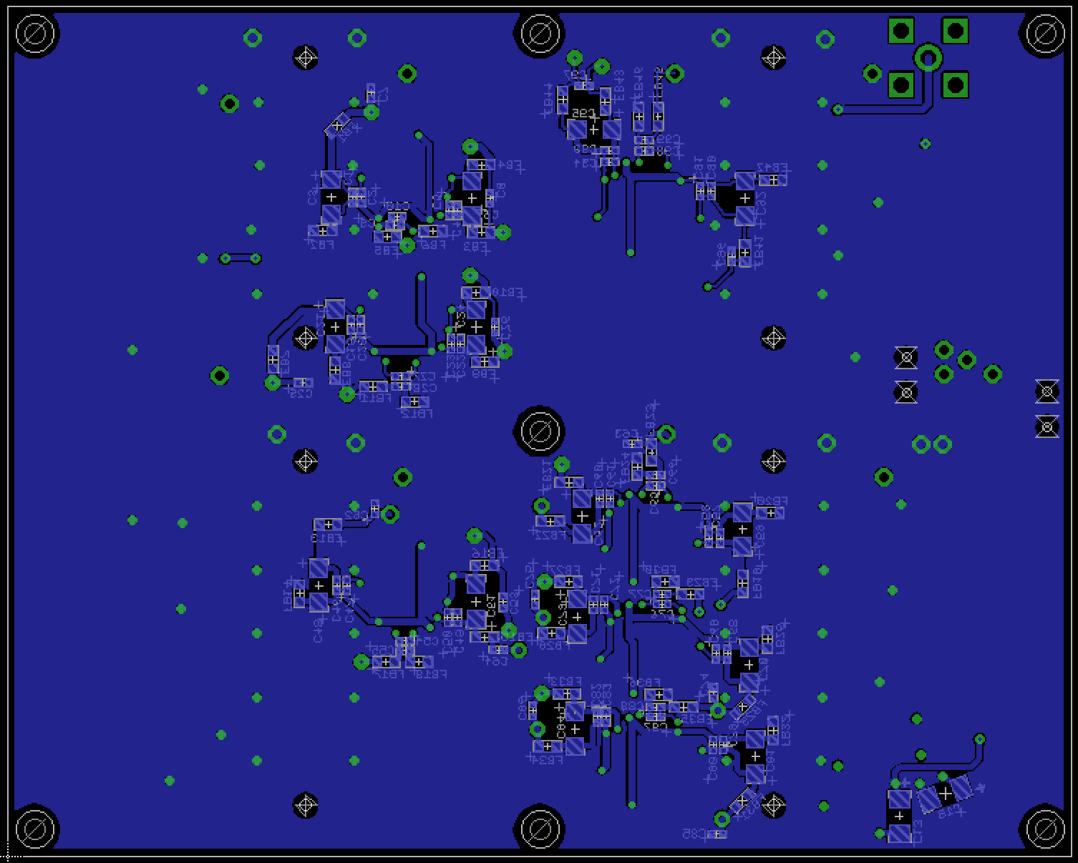
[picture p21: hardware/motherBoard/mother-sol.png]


### Parts List

Part  | Value  | Device  | Package  | Description
--|---|---|---|--
C1   |  0.1u           |  C1005            | 1005           |    
C2   |  1000p          |  C1005            | 1005           |    
C3   |  33u            |  C_POLAR3216      | 3216_POLAR     |    
C4   |  0.1u           |  C1005            | 1005           |    
C5   |  1000p          |  C1005            | 1005           |    
C6   |  33u            |  C_POLAR3216      | 3216_POLAR     |    
C7   |  0.1u           |  C1005            | 1005           |    
C8   |  0.1u           |  C1005            | 1005           |    
C9   |  1000p          |  C1005            | 1005           |    
C10  |  0.1u           |  C1005            | 1005           |    
C11  |  0.1u           |  C1005            | 1005           |    
C12  |  20p            |  C1005            | 1005           |    
C13  |  10uF           |  C_POLAR          | 3216_POLAR     |    
C14  |  0.1uF          |  C1005            | 1005           |    
C15  |  10uF           |  C_POLAR          | 3216_POLAR     |    
C16  |  0.1u           |  C1005            | 1005           |    
C17  |  0.1u           |  C1005            | 1005           |    
C18  |  0.1u           |  C1005            | 1005           |    
C19  |  0.1u           |  C1005            | 1005           |    
C20  |  1000p          |  C1005            | 1005           |    
C21  |  33u            |  C_POLAR3216      | 3216_POLAR     |    
C22  |  0.1u           |  C1005            | 1005           |    
C23  |  1000p          |  C1005            | 1005           |    
C24  |  33u            |  C_POLAR3216      | 3216_POLAR     |    
C25  |  0.1u           |  C1005            | 1005           |    
C26  |  0.1u           |  C1005            | 1005           |    
C27  |  1000p          |  C1005            | 1005           |    
C28  |  0.1u           |  C1005            | 1005           |    
C29  |  0.1u           |  C1005            | 1005           |    
C30  |  33u            |  C_POLAR          | 3216_POLAR     |    
C31  |  33u            |  C_POLAR          | 3216_POLAR     |    
C32  |  0.01u          |  C1608            | 1608           |    
C33  |  0.01u          |  C1608            | 1608           |    
C34  |  33u            |  C_POLAR          | 3216_POLAR     |    
C35  |  33u            |  C_POLAR          | 3216_POLAR     |    
C36  |  0.01u          |  C1608            | 1608           |    
C37  |  0.01u          |  C1608            | 1608           |    
C38  |  33u            |  C_POLAR          | 3216_POLAR     |    
C39  |  33u            |  C_POLAR          | 3216_POLAR     |    
C40  |  0.01u          |  C1608            | 1608           |    
C41  |  0.01u          |  C1608            | 1608           |    
C42  |  33u            |  C_POLAR          | 3216_POLAR     |    
C43  |  33u            |  C_POLAR          | 3216_POLAR     |    
C44  |  0.01u          |  C1608            | 1608           |    
C45  |  0.01u          |  C1608            | 1608           |    
C46  |  0.1u           |  C1005            | 1005           |    
C47  |  1000p          |  C1005            | 1005           |    
C48  |  33u            |  C_POLAR3216      | 3216_POLAR     |    
C49  |  0.1u           |  C1005            | 1005           |    
C50  |  1000p          |  C1005            | 1005           |    
C51  |  33u            |  C_POLAR3216      | 3216_POLAR     |    
C52  |  0.1u           |  C1005            | 1005           |    
C53  |  0.1u           |  C1005            | 1005           |    
C54  |  1000p          |  C1005            | 1005           |    
C55  |  0.1u           |  C1005            | 1005           |    
C56  |  0.1u           |  C1005            | 1005           |    
C57  |  0.1u           |  C1005            | 1005           |    
C58  |  1000p          |  C1005            | 1005           |    
C59  |  33u            |  C_POLAR3216      | 3216_POLAR     |    
C60  |  0.1u           |  C1005            | 1005           |    
C61  |  1000p          |  C1005            | 1005           |    
C62  |  33u            |  C_POLAR3216      | 3216_POLAR     |    
C63  |  0.1u           |  C1005            | 1005           |    
C64  |  0.1u           |  C1005            | 1005           |    
C65  |  1000p          |  C1005            | 1005           |    
C66  |  0.1u           |  C1005            | 1005           |    
C67  |  0.1u           |  C1005            | 1005           |    
C68  |  0.1u           |  C1005            | 1005           |    
C69  |  1000p          |  C1005            | 1005           |    
C70  |  33u            |  C_POLAR3216      | 3216_POLAR     |    
C71  |  0.1u           |  C1005            | 1005           |    
C72  |  1000p          |  C1005            | 1005           |    
C73  |  33u            |  C_POLAR3216      | 3216_POLAR     |    
C74  |  0.1u           |  C1005            | 1005           |    
C75  |  0.1u           |  C1005            | 1005           |    
C76  |  1000p          |  C1005            | 1005           |    
C77  |  0.1u           |  C1005            | 1005           |    
C78  |  0.1u           |  C1005            | 1005           |    
C79  |  0.1u           |  C1005            | 1005           |    
C80  |  1000p          |  C1005            | 1005           |    
C81  |  33u            |  C_POLAR3216      | 3216_POLAR     |    
C82  |  0.1u           |  C1005            | 1005           |    
C83  |  1000p          |  C1005            | 1005           |    
C84  |  33u            |  C_POLAR3216      | 3216_POLAR     |    
C85  |  0.1u           |  C1005            | 1005           |    
C86  |  0.1u           |  C1005            | 1005           |    
C87  |  1000p          |  C1005            | 1005           |    
C88  |  0.1u           |  C1005            | 1005           |    
C89  |  0.1u           |  C1005            | 1005           |    
C90  |  0.1u           |  C1005            | 1005           |    
C91  |  1000p          |  C1005            | 1005           |    
C92  |  33u            |  C_POLAR3216      | 3216_POLAR     |    
C93  |  0.1u           |  C1005            | 1005           |    
C94  |  1000p          |  C1005            | 1005           |    
C95  |  33u            |  C_POLAR3216      | 3216_POLAR     |    
C96  |  0.1u           |  C1005            | 1005           |    
C97  |  0.1u           |  C1005            | 1005           |    
C98  |  1000p          |  C1005            | 1005           |    
C99  |  0.1u           |  C1005            | 1005           |    
C100 |  0.1u           |  C1005            | 1005           |    
CN1  |  |  FX10A-80S/8-SV   |              |   HIROSE
CN2  |  |  FX10A-80S/8-SV   |              |   HIROSE
CN3  |  |  FX10A-100S/10-SV |              |   HIROSE
CN4  |  |  FX10A-100S/10-SV |              |   HIROSE
CN5  |  |  FH12-30S-0.5SH   | FPC_30         | HIROSE   
CN6  |  |  FH12-30S-0.5SH   | FPC_30         | HIROSE   
CN7  |  |  FH12-30S-0.5SH   | FPC_30         | HIROSE   
CN8  |  |  U.FL-R-SMT       | U.FL-R-SMT     | HIROSE   
CN9  |  |  U.FL-R-SMT       | U.FL-R-SMT     | HIROSE   
CN10 |  |  U.FL-R-SMT       | U.FL-R-SMT     | HIROSE   
CN11 |  |  U.FL-R-SMT       | U.FL-R-SMT     | HIROSE   
CN12 |  |  U.FL-R-SMT       | U.FL-R-SMT     | HIROSE   
CN13 |  |  U.FL-R-SMT       | U.FL-R-SMT     | HIROSE   
CN14 |  |  U.FL-R-SMT       | U.FL-R-SMT     | HIROSE   
CN15 |  |  U.FL-R-SMT       | U.FL-R-SMT     | HIROSE   
CN16 |  |  FH12-30S-0.5SH   | FPC_30         | HIROSE   
CN17 |  |  FH12-30S-0.5SH   | FPC_30         | HIROSE   
CN18 |  |      | SMA_STRAIGHT   |             
CN19 |    |  DF13-2P-1.25V    | DF13-2P-12.5V  | HIROSE    
CN20 |    |  DF13-2P-1.25V    | DF13-2P-12.5V  | HIROSE    
CN21 |    |  U.FL-R-SMT       | U.FL-R-SMT     | HIROSE    
FB1  |  30 Ohm @ 100 MHz   |  MPZ1608S300A   | 1608           | Ferrite bead (TDK)
FB2  |  30 Ohm @ 100 MHz   |  MPZ1608S300A   | 1608           | Ferrite bead (TDK)
FB3  |  30 Ohm @ 100 MHz   |  MPZ1608S300A   | 1608           | Ferrite bead (TDK)
FB4  |  30 Ohm @ 100 MHz   |  MPZ1608S300A   | 1608           | Ferrite bead (TDK)
FB5  |  30 Ohm @ 100 MHz   |  MPZ1608S300A   | 1608           | Ferrite bead (TDK)
FB6  |  30 Ohm @ 100 MHz   |  MPZ1608S300A   | 1608           | Ferrite bead (TDK)
FB7  |  30 Ohm @ 100 MHz   |  MPZ1608S300A   | 1608           | Ferrite bead (TDK)
FB8  |  30 Ohm @ 100 MHz   |  MPZ1608S300A   | 1608           | Ferrite bead (TDK)
FB9  |  30 Ohm @ 100 MHz   |  MPZ1608S300A   | 1608           | Ferrite bead (TDK)
FB10 |  30 Ohm @ 100 MHz   |  MPZ1608S300A   | 1608           | Ferrite bead (TDK)
FB11 |  30 Ohm @ 100 MHz   |  MPZ1608S300A   | 1608           | Ferrite bead (TDK)
FB12 |  30 Ohm @ 100 MHz   |  MPZ1608S300A   | 1608           | Ferrite bead (TDK)
FB13 |  30 Ohm @ 100 MHz   |  MPZ1608S300A   | 1608           | Ferrite bead (TDK)
FB14 |  30 Ohm @ 100 MHz   |  MPZ1608S300A   | 1608           | Ferrite bead (TDK)
FB15 |  30 Ohm @ 100 MHz   |  MPZ1608S300A   | 1608           | Ferrite bead (TDK)
FB16 |  30 Ohm @ 100 MHz   |  MPZ1608S300A   | 1608           | Ferrite bead (TDK)
FB17 |  30 Ohm @ 100 MHz   |  MPZ1608S300A   | 1608           | Ferrite bead (TDK)
FB18 |  30 Ohm @ 100 MHz   |  MPZ1608S300A   | 1608           | Ferrite bead (TDK)
FB19 |  30 Ohm @ 100 MHz   |  MPZ1608S300A   | 1608           | Ferrite bead (TDK)
FB20 |  30 Ohm @ 100 MHz   |  MPZ1608S300A   | 1608           | Ferrite bead (TDK)
FB21 |  30 Ohm @ 100 MHz   |  MPZ1608S300A   | 1608           | Ferrite bead (TDK)
FB22 |  30 Ohm @ 100 MHz   |  MPZ1608S300A   | 1608           | Ferrite bead (TDK)
FB23 |  30 Ohm @ 100 MHz   |  MPZ1608S300A   | 1608           | Ferrite bead (TDK)
FB24 |  30 Ohm @ 100 MHz   |  MPZ1608S300A   | 1608           | Ferrite bead (TDK)
FB25 |  30 Ohm @ 100 MHz   |  MPZ1608S300A   | 1608           | Ferrite bead (TDK)
FB26 |  30 Ohm @ 100 MHz   |  MPZ1608S300A   | 1608           | Ferrite bead (TDK)
FB27 |  30 Ohm @ 100 MHz   |  MPZ1608S300A   | 1608           | Ferrite bead (TDK)
FB28 |  30 Ohm @ 100 MHz   |  MPZ1608S300A   | 1608           | Ferrite bead (TDK)
FB29 |  30 Ohm @ 100 MHz   |  MPZ1608S300A   | 1608           | Ferrite bead (TDK)
FB30 |  30 Ohm @ 100 MHz   |  MPZ1608S300A   | 1608           | Ferrite bead (TDK)
FB31 |  30 Ohm @ 100 MHz   |  MPZ1608S300A   | 1608           | Ferrite bead (TDK)
FB32 |  30 Ohm @ 100 MHz   |  MPZ1608S300A   | 1608           | Ferrite bead (TDK)
FB33 |  30 Ohm @ 100 MHz   |  MPZ1608S300A   | 1608           | Ferrite bead (TDK)
FB34 |  30 Ohm @ 100 MHz   |  MPZ1608S300A   | 1608           | Ferrite bead (TDK)
FB35 |  30 Ohm @ 100 MHz   |  MPZ1608S300A   | 1608           | Ferrite bead (TDK)
FB36 |  30 Ohm @ 100 MHz   |  MPZ1608S300A   | 1608           | Ferrite bead (TDK)
FB37 |  30 Ohm @ 100 MHz   |  MPZ1608S300A   | 1608           | Ferrite bead (TDK)
FB38 |  30 Ohm @ 100 MHz   |  MPZ1608S300A   | 1608           | Ferrite bead (TDK)
FB39 |  30 Ohm @ 100 MHz   |  MPZ1608S300A   | 1608           | Ferrite bead (TDK)
FB40 |  30 Ohm @ 100 MHz   |  MPZ1608S300A   | 1608           | Ferrite bead (TDK)
FB41 |  30 Ohm @ 100 MHz   |  MPZ1608S300A   | 1608           | Ferrite bead (TDK)
FB42 |  30 Ohm @ 100 MHz   |  MPZ1608S300A   | 1608           | Ferrite bead (TDK)
FB43 |  30 Ohm @ 100 MHz   |  MPZ1608S300A   | 1608           | Ferrite bead (TDK)
FB44 |  30 Ohm @ 100 MHz   |  MPZ1608S300A   | 1608           | Ferrite bead (TDK)
FB45 |  30 Ohm @ 100 MHz   |  MPZ1608S300A   | 1608           | Ferrite bead (TDK)
FB46 |  30 Ohm @ 100 MHz   |  MPZ1608S300A   | 1608           | Ferrite bead (TDK)
R1   |  2k             |  R1005            | 1005           |             
R2   |  33             |  R1005            | 1005           |             
R3   |  33             |  R1005            | 1005           |             
R4   |  1k             |  R1005            | 1005           |             
R5   |  2k             |  R1005            | 1005           |             
R6   |  2k             |  R1005            | 1005           |             
R7   |  2k             |  R1005            | 1005           |             
R8   |  2k             |  R1005            | 1005           |             
R9   |  50             |  R1005            | 1005           |             
R10  |  100            |  R1005            | 1005           |             
R11  |  2k             |  R1005            | 1005           |             
R12  |  50             |  R1005            | 1005           |             
R13  |  100            |  R1005            | 1005           |             
R14  |  2k             |  R1005            | 1005           |             
R15  |  50             |  R1005            | 1005           |             
R16  |  100            |  R1005            | 1005           |             
R17  |  2k             |  R1005            | 1005           |             
R18  |  50             |  R1005            | 1005           |             
R19  |  100            |  R1005            | 1005           |             
T1   |          |  TC1-1T+          | AT224          | Mini Circuits     
T2   |          |  TC1-1T+          | AT224          | Mini Circuits     
T3   |          |  TC1-1T+          | AT224          | Mini Circuits     
T4   |          |  TC1-1T+          | AT224          | Mini Circuits            
U1   |       |  AD9740ACPZ       | 32-Lead LFCSP_VQ  | Analog Devices            
U2   |       |  AD9740ACPZ       | 32-Lead LFCSP_VQ  | Analog Devices            
U3   |       |  AD9740ACPZ       | 32-Lead LFCSP_VQ  | Analog Devices            
U4   |       |  AD9740ACPZ       | 32-Lead LFCSP_VQ  | Analog Devices            
U5   |       |  AD9740ACPZ       | 32-Lead LFCSP_VQ  | Analog Devices            
U6   |       |  AD9740ACPZ       | 32-Lead LFCSP_VQ  | Analog Devices            
U7   |       |  AD9245BCPZ-80    | 32-Lead LFCSP_WQ  | Analog Devices            
U8   |       |  AD9740ACPZ       | 32-Lead LFCSP_VQ  | Analog Devices            

- LFCSP: Lead Frame Chip Scale Package

- - -
<table>
<tr><td><b>Qty</b></td><td><b>Value</b></td><td><b>Device</b></td><td><b>Parts</b></td></tr>
<tr><td>8</td><td>0.01u</td><td>C (1608)</td><td>C32, C33, C36, C37, C40, C41, C44, C45</td></tr>
<tr><td>45</td><td>0.1u</td><td>C (1005)</td><td>C1, C4, C7, C8, C10, C11, C16, C17, C18, C19, C22, C25, C26, C28, C29, C46, C49, C52, C53, C55, C56, C57, C60, C63, C64, C66, C67, C68, C71, C74, C75, C77, C78, C79, C82, C85, C86, C88, C89, C90, C93, C96, C97, C99, C100</td></tr>
<tr><td>1</td><td>0.1uF</td><td>C (1005)</td><td>C14</td></tr>
<tr><td>1</td><td>1k</td><td>R (1005)</td><td>R4</td></tr>
<tr><td>8</td><td>2k</td><td>R (1005)</td><td>R1, R5, R6, R7, R8, R11, R14, R17</td></tr>
<tr><td>2</td><td>10uF</td><td>C (polar, 3216)</td><td>C13, C15</td></tr>
<tr><td>1</td><td>20p</td><td>C (1005)</td><td>C12</td></tr>
<tr><td>2</td><td>33</td><td>R (1005)</td><td>R2, R3</td></tr>
<tr><td>8</td><td>33u</td><td>C (polar, 3216)</td><td>C30, C31, C34, C35, C38, C39, C42, C43</td></tr>
<tr><td>14</td><td>33u</td><td>C (polar, 3216)</td><td>C3, C6, C21, C24, C48, C51, C59, C62, C70, C73, C81, C84, C92, C95</td></tr>
<tr><td>4</td><td>50</td><td>R (1005)</td><td>R9, R12, R15, R18</td></tr>
<tr><td>4</td><td>100</td><td>R (1005)</td><td>R10, R13, R16, R19</td></tr>
<tr><td>21</td><td>1000p</td><td>C (1005)</td><td>C2, C5, C9, C20, C23, C27, C47, C50, C54, C58, C61, C65, C69, C72, C76, C80, C83, C87, C91, C94, C98</td></tr>
<tr><td>1</td><td></td><td>AD9245BCPZ-80 (Analog Devices)</td><td>U7</td></tr>
<tr><td>7</td><td></td><td>AD9740ACPZ (Analog Devices)</td><td>U1, U2, U3, U4, U5, U6, U8</td></tr>
<tr><td>2</td><td></td><td>DF13-2P-1.25V (HIROSE)</td><td>CN19, CN20</td></tr>
<tr><td>46</td><td></td><td>FERRITE BEAD</td><td>FB1, FB2, FB3, FB4, FB5, FB6, FB7, FB8, FB9, FB10, FB11, FB12, FB13, FB14, FB15, FB16, FB17, FB18, FB19, FB20, FB21, FB22, FB23, FB24, FB25, FB26, FB27, FB28, FB29, FB30, FB31, FB32, FB33, FB34, FB35, FB36, FB37, FB38, FB39, FB40, FB41, FB42, FB43, FB44, FB45, FB46</td></tr>
<tr><td>5</td><td></td><td>FH12-30S-0.5SH (HIROSE)</td><td>CN5, CN6, CN7, CN16, CN17</td></tr>
<tr><td>2</td><td></td><td>FX10A-80S/8-SV (HIROSE)</td><td>CN1, CN2</td></tr>
<tr><td>2</td><td></td><td>FX10A-100S/10-SV (HIROSE)</td><td>CN3, CN4</td></tr>
<tr><td>1</td><td></td><td>SMA STRAIGHT</td><td>CN18</td></tr>
<tr><td>4</td><td></td><td>TC1-1T+ (Mini-Circuits)</td><td>T1, T2, T3, T4</td></tr>
<tr><td>9</td><td></td><td>U.FL-R-SMT (HIROSE)</td><td>CN8, CN9, CN10, CN11, CN12, CN13, CN14, CN15, CN21</td></tr>
</table>

- - -
[Back to Home](../../index.md)

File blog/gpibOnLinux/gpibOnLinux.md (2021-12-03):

---

# GPIB setup on Linux
- 3 Dec 2021 Revised by Kazuyuki Takeda  
- 14 Mar 2019 Revised by Kazuyuki Takeda  
- 12 Oct 2018 Revised by Kazuyuki Takeda  
- 21 May 2018 Written by Kazuyuki Takeda  

## Introduction
We want to make remote control over the power supply for our cryogen-free superconducting magnet (SMS80C, Cryogenics) on the console software of Opencore NMR 2. I have attempted to program on Windows for a while, but never succeeded, and gave up. Now I decided to program on Linux.

## Our GPIB
- Measurement computing
- USB-488
- Default primary address: 4

## Driver compilation (Cent OS)
##### linux-gpib-4.1.0  
- `linux-gpib-4.1.0` was downloaded from [http://linux-gpib.sourceforge.net](http://linux-gpib.sourceforge.net) and extracted in an arbitrary working directory.
- `./configure`
- `make`

##### linux-gpib-4.2.0
- If you download the latest (at the time of writing, Mar 2019) version (linux-gpib-4.2.0) and try to compile in the same way as the above example, you may get an error `implicit declaration of function ‘of_find_node_by_path’`, and the compilation may stop.  
- A remedy is suggested [here](https://sourceforge.net/p/linux-gpib/mailman/message/36479049/).  
- In short, you need to open `drivers/gpib/Makefile` with a text editor and comment out the line `obj-y += fmh_gpib/`  
- Then, compilation should work.  

## Installation and setup
- `sudo make install`
- And the kernel driver module is `ni_usb_gpib.ko`, and the board type, to be described in `/etc/gpib.conf`, is `ni_usb_b`.
- Driver file `ni_usb_gpib.ko` has been created upon successful compilation. To install, I went into the directory that contains it and ran `sudo modprobe ni_usb_gpib`. To verify the driver has really been installed, I checked with `lsmod | grep gpib`.
- Next, we needed to edit `/etc/gpib.conf` as follows:

```
interface {
        minor = 0       /* board index, minor = 0 uses /dev/gpib0, minor = 1 uses /dev/gpib1, etc. */
        board_type = "ni_usb_b" /* type of interface board being used */
        name = "current"        /* optional name, allows you to get a board descriptor using ibfind() */
        pad = 0 /* primary address of interface             */
        sad = 4 /* secondary address of interface           */
        timeout = T10s  /* timeout for commands */
        eos = 0xda      /* EOS Byte, 0xa is newline and 0xd is carriage return */
        set-reos = yes  /* Terminate read if EOS */
        set-bin = no    /* Compare EOS 8-bit */
        set-xeos = no   /* Assert EOI whenever EOS byte is sent */
        set-eot = no    /* Assert EOI with last byte on writes */
        master = yes    /* interface board is system controller */
}
```

- name = `current` should be arbitrary (optionally used for `ibfind` function).
- `pad=0` and `sad=4` were necessary, with the dip-switched primary address on the current controller being 4. And in the program coding, it was necessary to set pad to be 4. My guess is: the primary address **to be set on the operating system** is relevant to the GPIB-USB adapter (in our case, we are using a single adapter, so that the address is the youngest, i.e., zero), whereas on the software we are supposed to connect **to the device** (in our case, the magnet power supply whose address is set on the dip switch on the pear panel to be 4).
- After saving the `gpib.conf` file, I ran `sudo gpib_config`, which makes setup according to the above `gpib.conf` file.
- Found in `linux-gpib-4.1.0/lib/gpib_config`.

## Without sudo...
Go to `/dev`, and `sudo chmod a+rw ./gpib0`.

## TODO
To realize plug and play, udev needs to be configured to (i) change the mode of /dev/gpib0 to 0666, and (ii) implement gpib_config. I will try to work it out and update this page (12 Oct 2018).

- - -

[Back](../index.md)

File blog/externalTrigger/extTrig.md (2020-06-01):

# Waiting for external trigger

12 May 2020 Typo error corrected by KT (exttrig)  
8 Mar 2019 Revised by Kazuyuki Takeda  

- - -

Warning: Do not put extremely high voltage into trigger pin, since it is connected directly to FPGA and can damage it!

To pause implementation of the pulse programmer until the spectrometer receives external trigger signal, use `exttrig` command.

```
Init
  pulse(pw1; gate1, gate2, ...)
  exttrig
  pulse(pw2; gate3, gate4, ...)
Relax
```

Trigger signal is to be fed to CN19 of the mother board. 

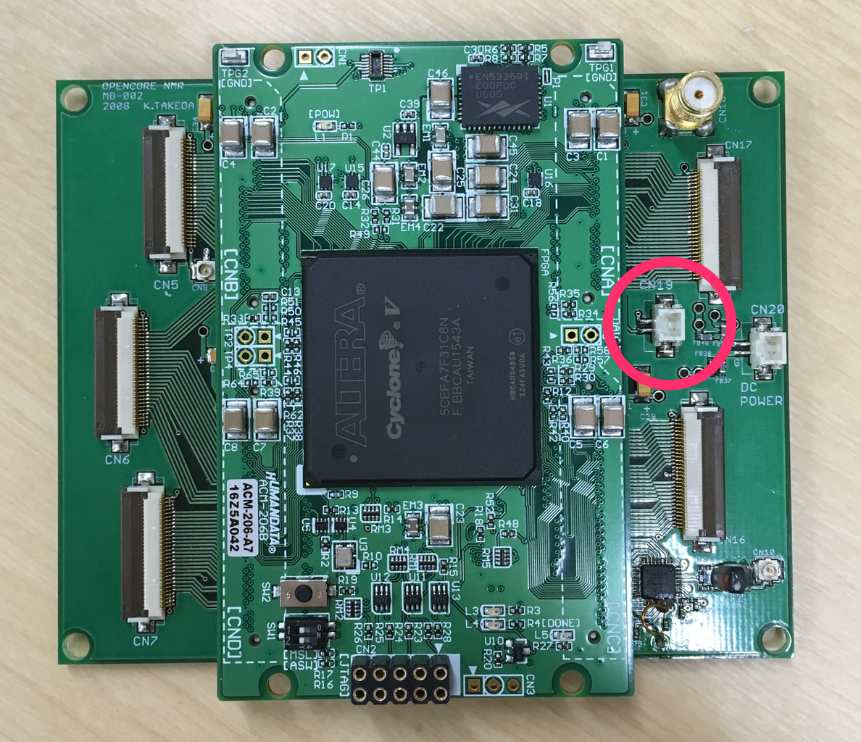
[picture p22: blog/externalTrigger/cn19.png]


The following is how one may connect a source of trigger pulse to the pin (note the proper orientation of wires on the CN19 pin!):

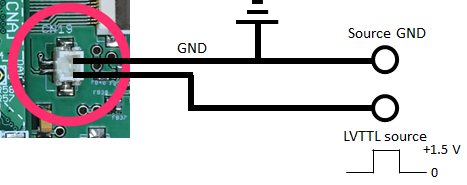
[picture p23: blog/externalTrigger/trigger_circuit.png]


It is designed to trigger with LVTTL pulse, but experimentally has been found to trigger so long as it receives a roughly square pulse exceeding +1.25 V. As the pin is directly connected to the FPGA, it is recommended not to put high voltage into this pin or else FPGA will be damaged! (+1.5 V square pulse is more than enough to trigger measurement!)

- - -

The following is an example trigger event. A (quite irregular) square pulse of +1.5 V amplitude (yellow) is used to trigger a 15 us 40 MHz rf pulse from the Opencore (blue). The code used is:

```
Init
  exttrig
  pulse(pw1; gate1, gate2, ...)
Relax
```

Though it seems there is a delay between the trigger and the pulse, if one zooms into the trigger in the second figure there is actually almost no delay between reaching the +1.25 V trigger level and firing the pulse.

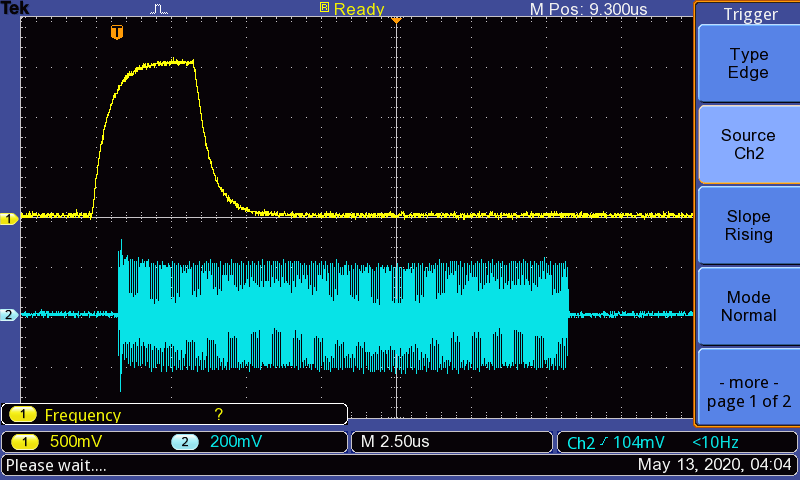
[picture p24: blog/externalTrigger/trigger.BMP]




As can be seen in the second figure, the rf pulse immediately fires upon the trigger reaching the +1.25 V level, and from the timescale, seems to indicate that the rf pulse will fire faster than at least 50 ns after the trigger level (+1.25 V) is reached.

[Back](../../index.md)

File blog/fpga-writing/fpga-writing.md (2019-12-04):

# FPGA Writing
1 Aug 2019 by Kazuyuki Takeda
- - -

##### We assume that
- The compiled (and converted) core-module file, such as `build2009c-cyclone5.jic`, has already been downloaded ([download](https://github.com/opencorenmr/fpga-devel-2.0.1/blob/master/cyclone5/output_files/)),  
- The FPGA board, ACM-206-A7 (HumanData) is powered,  
- A download cable (e.g., Terasic Blaster) is connected, and  
- The Quartus software has been launched.  



### Step-by-step instruction
- Run the ***Programmer*** from within the Quartus software. This can be done either by pull-down `Tools -> Programmer`, or by clicking an ***Programmer*** icon on the toolbar.
  

- The downloading hardware needs to be recognized. If not, click `Hardware Setup...`, and try to detect the download tool. In the screenshot below, `USB-Blaster [2-2.2]` is detected.

- Next, click `Auto Detect`. After a while, candidates may be displayd. Choose the FPGA that you actually use, and click `OK`. In this example, I use 5CEFA77F31C8N (Cyclone 5), and thus choose `CEFA7`.

- Select the top item in the list view (blue-highlighted in the screenshot below.). Click `Change File...` and choose the core-module file. Then, check `Program/Configure`, `Verify`, and `Blank-Check`, as shown in the screenshot.

- Click `Start`, and wait for a while. The progress bar should show a message "Success".
- Unplug the ribbon cable and disconnect the power supply. The FPGA will work the next time you switch the power supply on. ***Note that you need to switch off and on the power supply for the FPGA to be configured as intended.*** 

- - -
[Back](../../index.md)

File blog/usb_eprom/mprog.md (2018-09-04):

# Writing EPROM on USB board  
3 Sep 2018 Kazuyuki Takeda  

## EPROM configuration using MProg
- It seems only Windows can do this USB configuration procedure (I myself do this on a virtual Windows system running on Mac using VMWare Fusion). Nevertheless, **once the EPROM has been configured, you can use Mac and Linux as well!**
- Go to [FTDI's site](http://www.ftdichip.com/Support/Utilities.htm#MProg) and download **MProg** software.  
- Download [opencore-usb.ept (opencore usb configuration file)](opencore-usb.ept).  
- Connect the USB board of the Opencore NMR spectrometer.  
u
- Launch MProg.exe, connect the USB board, and click the magnifying glass icon.  
  
- If you connect this board for the first time, you should get a message saying that the number of blank devices is 1 and that of programmed devices is 0.
- Open the opencore-usb.ept. Then, parameters should have been set as shown in the figure.

- Finally, click the lightning-bolt icon to write these parameters in the EPROM on the board.  
  
- If you get a message like "Programmed Serial Number: ...", this board is ready for use!

- - -
[Back](../../index.md)
- - -

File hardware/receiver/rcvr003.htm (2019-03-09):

Partlist exported from /Users/takezo/work/opencoreNMR/circuitBoards/projects/NMR-RCVR/003/rcvr003.sch at 2019/03/08 14:37

Assembly variant:

Part | Value | Device | Package | Description
C1 | 10u | C_POLAR3216 | 3216_POLAR
C2 | 0.01u | C1005 | 1005 | CAPACITOR
C3 | 0.1u | C1005 | 1005 | CAPACITOR
C4 | 0.1u | C1005 | 1005 | CAPACITOR
C5 | 0.1u | C1005 | 1005 | CAPACITOR
C6 | 0.1u | C1005 | 1005 | CAPACITOR
C7 | 0.01u | C1005 | 1005 | CAPACITOR
C8 | 0.01u | C1608 | 1608 | CAPACITOR
C9 | 10u | C_POLAR3216 | 3216_POLAR
CN1 | SMASTRAIGHT | SMASTRAIGHT | SMA_STRAIGHT
CN2 | | U.FL-R-SMT | U.FL-R-SMT
CN3 | | U.FL-R-SMT | U.FL-R-SMT
CN4 | DF13-2P-1.25V | DF13-2P-1.25V | DF13-2P-12.5V
CN5 | | DF13-2P-1.25V | DF13-2P-12.5V
CN6 | | DF13-3P-1.25V | DF13-3P-1.25V
CN7 | DF13-2P-1.25V | DF13-2P-1.25V | DF13-2P-12.5V
CN8 | | U.FL-R-SMT | U.FL-R-SMT
CN9 | | U.FL-R-SMT | U.FL-R-SMT
CN10 | | U.FL-R-SMT | U.FL-R-SMT
CN11 | | U.FL-R-SMT | U.FL-R-SMT
CN12 | | U.FL-R-SMT | U.FL-R-SMT
FB2 | FERRITEBEAD | FERRITEBEAD | 1608
R1 | 510 | R1608 | 1608
R2 | 68 | R1608 | 1608
R3 | 68 | R1608 | 1608
R4 | 10 | R1005 | 1005
R5 | 10 | R1005 | 1005
R6 | 10 | R1005 | 1005
R7 | 10 | R1005 | 1005
R8 | 100 | R1608 | 1608
T1 | TC4-1W+ | TC4-1W+ | AT224
T2 | TC1-1-13M+ | TC1-1-13M+ | AT224
T3 | TC4-1W+ | TC4-1W+ | AT224
U1 | AD8343 | AD8343 | AD8343
U2 | MC74VHC1G04 | MC74VHC1G04 | MC74VHC1G04
U3 | ADG904 | ADG904 | ADG904_TSSOP

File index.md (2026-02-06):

{% include head.html %}

# Welcome to opencorenmr.github.io

This site serves for a _complementary_ role to [Opencore NMR2](http://kuchem.kyoto-u.ac.jp/bun/indiv/takezo/opencorenmr2/index.html).

I will be trying to add information on:
 - Hardware
 - Software
 - Pulse programming, and
 - Application examples.

- - -

# Software
- [Download](https://github.com/opencorenmr/console-devel-2.0.1/releases/)  

- - -

# Hardware

- [10MHz Clock](hardware/10MCLK/10MCLK.md) (14 Mar 2019)  
- [Mother board](hardware/motherBoard/motherBoard.md) (23 Feb 2019)  
- [DDS2](hardware/DDS2/DDS2.md) (2 Mar 2019)  
- [USB](hardware/USB/USB.md) (5 Mar 2019)  
- [Receiver](hardware/receiver/receiver.md) (9 Mar 2019)  
- [Filters](hardware/makingFilters/makingFilters.md) (9 Mar 2019)  

- - -

# Blog
- [New features of pulse programming language](blog/ppg-new2026feb/ppg-new2026feb.md) (6 Feb 2026)
- [Qt startup error on Linux](blog/Qt-startup-error/Qt-startup-error.md) (26 Dec 2019)  
- [FPGA writing](blog/fpga-writing/fpga-writing.md) (1 Aug 2019)  
- [Device driver](blog/driverSetup/driverSetup.md) (1 Aug 2019)  
- [GPIB on Linux](blog/gpibOnLinux/gpibOnLinux.md) (14 Mar 2019)  
- [Qt on Linux](blog/qt-on-linux/qt-on-linux.md) (14 Mar 2019)   
- [Frequency control](blog/dds2/dds2.md) (30 Jan 2019)  
- [Data files](blog/dataFiles/dataFiles.md) (29 Jan 2019)  
- [Gate definition](blog/gateDefinition/gateDefinition.md) (29 Jan 2019)  
- [Kinds of gates](blog/kindsOfGates/kindsOfGates.md) (29 Jan 2019)  
- [Shaped pulses](blog/shapedPulse/shapedPulse.md) (28 Jan 2019)  
- [Probe tuning](blog/probeTune/probeTune.md) (28 Jan 2019)  
- [Driver setup](blog/driverSetup/driverSetup.md) (11 Jan 2019)  
- [USB setup on Linux](blog/USBSetupOnLinux/USBSetupOnLinux.md) (15 Oct 2018)  
- [EPROM configuration on USB board](blog/usb_eprom/mprog.md) (3 Sep 2018)  
- [LAPACK compilation](blog/lapack/lapack.md) (28 Aug 2018)  
- [On-line and Off-line Experimental Settings](blog/onLineAndOffLineExpSettings/onLineAndOffLineExpSettings.md) (21 July 2018)  
- [Phase Cycling](blog/phaseCycle/phaseCycle.md)  
- [External trigger](blog/externalTrigger/extTrig.md)

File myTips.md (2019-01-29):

### Disableing the "View on GitHub" button
- `_config.yml`に以下を記述
```
github:
  is_project_page: false
```
- [参考](https://github.com/pages-themes/cayman/issues/29)  

### MathJax
- `_includes/head.html`を作成。以下の内容で。
```
 <script type="text/x-mathjax-config">
    MathJax.Hub.Config({
      tex2jax: {
        skipTags: ['script', 'noscript', 'style', 'textarea', 'pre'],
        inlineMath: [['$','$']]
      }
    });
  </script>
  <script src="https://cdn.mathjax.org/mathjax/latest/MathJax.js?config=TeX-AMS-MML_HTMLorMML" type="text/javascript"></script> 
```
- [参考](https://stackoverflow.com/questions/26275645/how-to-support-latex-in-github-pages)  
- でもこれだとインラインのみサポート？

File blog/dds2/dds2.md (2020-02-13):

# Frequency control on AD9858

13 Feb 2020 Revised by Kazuyuki Takeda  
30 Jan 2019 Kazuyuki Takeda

- - -
## Related Topics  
- [probe tuning](../probeTune/probeTune.md)   

## Introduction  
AD9858, a DDS chip (Analog Devices), is driven by a clock with a frequency of either 1 GHz or 2 GHz. Note that even with the latter option (2 GHz clock), the clock frequency is divided into two inside the chip, and the DDS core operates at a clock frequency of 1 GHz. Even though the functionality is identical whichever option you choose, we need to let the AD9858 chip know which you have actually chosen. In addition, there are various options, some of which we have to set in advance to implementation of pulse sequences. And of course, we need to send commands requesting the chip to generate a signal with a specified frequency. Furthermore, you may want to switch or sweep the frequency. In this section we take a look at how to do such settings.

## AD9858 register map  
Below I show an excerpted register map of AD9858: For a complete table, refer to the data sheet of AD9858 provided by Analog Devices.

address  | bit 7  | bit 6  | bit 5  | bit 4  | bit 3  | bit 2  | bit 1  | bit 0
:-:|:-:|:-:|:-:|:-:|:-:|:-:|:-:|:-:
0x00  |   | 2GHz Divider Disable  |   | Mixer Power Down  | Phase Detect PwrDwn  |   |   |  
0x01  | Freq. Sweep Enable  |   |   |   |   |   |   |  
0x02  | Auto Clr Freq. Accum.  |   |   |   |   |   |   |  
0x03  |   |   |   |   |   |   |   |  

## AD9858 gate definition  
We focus on the AD9858 chip in the first transmitter channel. Depending on the number of channels in your own Opencore NMR spectrometer, gate definitions for additional AD9858 chips dedicated for other channels may be required, but this can be done in a similar manner. In the gate definition file (for detail of the gate definition, refer to the previous section), we have several entries. First of all, a gate with “AD9858” kind is required. Here, we assume that the physical connections between the AD9858 pins and the output ports of the pulse programmer is as follows:

  FUD | WR  | ADD5  | ADD4  | ADD3   | ADD2  | ADD1  | ADD0  | D7  | D6  | D5  | D4  | D3  | D2  | D1  | D0
:-:|:-:|:-:|:-:|:-:|:-:|:-:|:-:|:-:|:-:|:-:|:-:|:-:|:-:|:-:|:-:
45  | 43  | 42  | 41  | 40  | 39  | 38  | 37  | 36  | 35  | 34  | 33  | 32  | 31  | 30  | 29  

We name the gate as “F1Freq”, and have the following entry in the gate definition file:
```
[F1Freq]
caption = frequency for channel 1
kind = AD9858
bitLength=16
channel = 1
F1Freq_0=29
F1Freq_1=30
F1Freq_2=31
F1Freq_3=32
F1Freq_4=33
F1Freq_5=34
F1Freq_6=35
F1Freq_7=36
F1Freq_8=37
F1Freq_9=38
F1Freq_10=39
F1Freq_11=40
F1Freq_12=41
F1Freq_13=42
F1Freq_14=43
F1Freq_15=45
```
We have two more definitions,
```
[F1FreqPS]
caption = AD9858 Profile Select for channel 1
channel = 1
bitLength = 2
kind = logic_vector
F1FreqPS_0 = 47
F1FreqPS_1 = 46
```
, and,
```
[F1FreqRST]
channel = 1
bitLength = 1
kind = logic
F1FreqRST_0 = 48
```

## Fixed-frequency experiments
Now, we can use in pulse programs the gates named `F1Freq`, `F1FreqPS`, and `F1FreqRST`. The first thing to do is initialization of AD9858.
```
pulse(1u; F1FreqRST)
```
This command sends the reset signal to the AD9858 chip for one microsecond. Upon reception of the reset signal, the chip forgets the previous settings. The time interval of one microsecond is arbitrary, and can be longer or shorter. Since the I/O synchronization clock (SYNCLK) is 1 GHz divided by 8 (i.e. 125 MHz), the pulse width can be as short as ~8 ns. But I think there is little point of setting such a short width that just manage to exceed the threshold.

Next, we want to disable 2 GHz clock divider, as we are using the 1 GHz clock. Recalling the register map of AD9858, we have the “2GHz Divider Disable” entry in the 6th bit of address “zero” (0x00). We also want to keep the default power-down options regarding to the analog mixer stage (4th bit) and the phase detector (3rd bit).

address  | bit 7  | bit 6  | bit 5  | bit 4  | bit 3  | bit 2  | bit 1  | bit 0
:-:|:-:|:-:|:-:|:-:|:-:|:-:|:-:|:-:
0x00  |   | 2GHz Divider Disable  |   | Mixer Power Down  | Phase Detect PwrDwn  |   |   |  

In addition, we activate the “WR” (write) flag, so that the resultant control bit sequence is as follows.

FUD | WR  | ADD5  | ADD4  | ADD3   | ADD2  | ADD1  | ADD0  | D7  | D6  | D5  | D4  | D3  | D2  | D1  | D0
:-:|:-:|:-:|:-:|:-:|:-:|:-:|:-:|:-:|:-:|:-:|:-:|:-:|:-:|:-:|:-:
0  | 1  | 0  | 0  | 0  | 0  | 0  | 0  | 0  | 1  | 0  | 1  | 1  | 0  | 0  | 0  

Note that all address bits (Add5..ADD0) are set to zero, as the current relevant address is “zero” (0x00). In this way, we get a binary number `0100000001011000`, which corresponds to `16472` in the decimal expression. We thus write
```
pulse(1u; F1Freq(setup; 16472))
```
(***Note***: this is specific to Opencore NMR 2. For the first (obsolete) version of Opencore NMR, this should be read as `pulse(1u; F1FreqSetup(16472))`)

You may define in the preamble of the pulse program an integer variable,
```
int AD9858_2GHz_DISABLE = 16472;
```
and then write
```
pulse(1u; F1Freq(setup; AD9858_2GHz_DISABLE))
```
There is no difference in the way that the AD9858 chip operates, but the usage of the variable may give you a feeling of what is going on, as compared to the “apparently” meaningless number.

Since the value of `AD9858_2GHz_DISABLE` would be fixed throughout the experiment, it would be nice if it is defined as a constant parameter:
```
const int AD9858_2GHz_DISABLE = 16472;
```
Now we are ready to set the frequency at the main output port of the AD9858 chip, like
```
pulse(1u; F1Freq(100.0))  // in MHz !or, equivalently
pulse(1u; F1Freq(0; 100.0))  // in MHz !
```
This is a command for frequency setting in profile #0. Upon compilation, five separate binary lines are generated to send a 32-bit frequency-tuning word. According to the datasheet of AD9858, the address map for the four profiles and delta-frequency tuning word (used for frequency sweep) is
- Profile 0: 0x0A..0x0D  
- Profile 1: 0x10..0x13  
- Profile 2: 0x16..0x19  
- Profile 3: 0x1C..0x1F  
- Delta-Freq Tuning: 0x04..0x07  

That is, to set frequencies of, say, 110, 120, and 130 MHz in profile 1, 2, and 3, we write
```
pulse(1u; F1Freq(1; 110.0))  // in MHz !
pulse(1u; F1Freq(2; 120.0))  // in MHz !
pulse(1u; F1Freq(3; 130.0))  // in MHz !and we can later select one of them by
pulse(pw; F1FreqPS(1)) // 1 may be replaced by 2 or 3.
```
For Delta-frequency tuning setting, we use “-1”:
```
pulse(1u; F1Freq(-1; 0.123))  // in MHz !
```
This option is relevant for frequency sweeping. See below for details.

## Frequency sweeping
In Opencore NMR2, the frequency sweeping can be implemented with `sweep` and `endSweep` commands. An example of such is described in the topic of [probe tuning](../probeTune/probeTune.md)

###### An example of frequency sweep
```
sweep(F1Freq(fCenter-fSpan/2,fCenter+fSpan/2))
  pulse(50n; ST, RG)
  pulse(dw*al; F1Amp(a), pl, F1_Gate, F1_Unblank, RG)  
  // any other commands, including pulse as well as loop, can be inserted.
endSweep(F1Freq)
```

For most users who just use the `sweep` and `endSweep` commands, it is not necessary to read the following discussions. Those who are eager to know what is happening behind and/or to customize frequency-sweep options may want to continue reading.

##### Enabling frequency sweep
We recall the register map of AD9858.

address  | bit 7  | bit 6  | bit 5  | bit 4  | bit 3  | bit 2  | bit 1  | bit 0
:-:|:-:|:-:|:-:|:-:|:-:|:-:|:-:|:-:
0x00  |   | 2GHz Divider Disable  |   | Mixer Power Down  | Phase Detect PwrDwn  |   |   |  
0x01  | Freq. Sweep Enable  |   |   |   |   |   |   |  
0x02  | Auto Clr Freq. Accum.  |   |   |   |   |   |   |  
0x03  |   |   |   |   |   |   |   |  

Here, we are interested in the “Freq. Sweep Enable” and “Auto Clr. Freq. Accum” registers. In addition, we need to set “Delta-Freq Tuning” located in addresses 0x04-0x07, and “Delta-Freq Ramp Rate” in 0x08-0x09.

| address |	|
| :-: | :-: |
| 0x04	| Delta Frequency Word <7:0> |
| 0x05	| Delta Frequency Word <15:8> |
| 0x06	| Delta Frequency Word <23:16> |
| 0x07	| Delta Frequency Word <31:24> |
| 0x08	| Delta Frequency Ramp Rate Word <7:0> |
| 0x09	| Delta Frequency Ramp Rate Word <15:8> |

To use the frequency-sweep function, we activate the “Freq. Sweep Enable” register. The relevant address is 0x01 (00001 in the binary expression), and we raise the 7th bit as well as the “”WR” register.

FUD | WR  | ADD5  | ADD4  | ADD3   | ADD2  | ADD1  | ADD0  | D7  | D6  | D5  | D4  | D3  | D2  | D1  | D0
:-:|:-:|:-:|:-:|:-:|:-:|:-:|:-:|:-:|:-:|:-:|:-:|:-:|:-:|:-:|:-:
0  | 1  | 0  | 0  | 0  | 0  | 0  | 1  | 1  | 0  | 0  | 0  | 0  | 0  | 0  | 0  

We thus have a binary number 0100000110000000, which corresponds to 16768 in the decimal expression. Hence, the command for enabling the frequency sweep is
```
pulse(1u; F1Freq(setup; 16768))
```
Or, we may prefer to define a parameter
```
const int FREQ_SWEEP_ENABLE = 16768;
```
in the preamble of the pulse program, and then write
```
pulse(1u; F1Freq(setup; FREQ_SWEEP_ENABLE))
```
Now, the setting has been written in the internal buffer register. To transfer the setting to the memory register of the AD9858 chip, the FUD (Frequency UpDate) signal is used.

FUD | WR  | ADD5  | ADD4  | ADD3   | ADD2  | ADD1  | ADD0  | D7  | D6  | D5  | D4  | D3  | D2  | D1  | D0
:-:|:-:|:-:|:-:|:-:|:-:|:-:|:-:|:-:|:-:|:-:|:-:|:-:|:-:|:-:|:-:
1  | 0  | 0  | 0  | 0  | 0  | 0  | 0  | 0  | 0  | 0  | 0  | 0  | 0  | 0  | 0  

```
pulse(1u; F1Freq(setup; 32768))
```
or,
```
pulse(1u; F1Freq(setup; FUD))
```
In the latter case, we need to define the FUD parameter in the preamble:
```
const int FUD=32768;
```
Note that the FUD signal may be sent in a later stage, when setting of other registers has been done. In addition, FUD is also activated upon usage of the “AD9858” gate (in the present case, the F1Freq gate.)

##### Setting the frequency-sweep rate
Next, we need to set the ramp rate of frequency sweep. For AD9858, the maximum rate is 125 MHz, at which the frequency is altered every 8 ns. The update interval should be given by 8 ns times “Delta Frequency Ramp Rate Word”. For example, to increment the frequency every 1 us, Delta Frequency Ramp Rate Word should be 1 us/8 ns = 125. In a 16-bit binary expression, 125 is 0000000001111101. We need to set the upper and lower 8 bits separately in addresses 0x08 and 0x09, together with the “WR” register:

FUD | WR  | ADD5  | ADD4  | ADD3   | ADD2  | ADD1  | ADD0  | D7  | D6  | D5  | D4  | D3  | D2  | D1  | D0
:-:|:-:|:-:|:-:|:-:|:-:|:-:|:-:|:-:|:-:|:-:|:-:|:-:|:-:|:-:|:-:
0  | 1  | 0  | 0  | 1  | 0  | 0  | 0  | 0  | 1  | 1  | 1  | 1  | 1  | 0  | 1  

FUD | WR  | ADD5  | ADD4  | ADD3   | ADD2  | ADD1  | ADD0  | D7  | D6  | D5  | D4  | D3  | D2  | D1  | D0
:-:|:-:|:-:|:-:|:-:|:-:|:-:|:-:|:-:|:-:|:-:|:-:|:-:|:-:|:-:|:-:
0  | 1  | 0  | 0  | 1  | 0  | 0  | 1  | 0  | 0  | 0  | 0  | 0  | 0  | 0  | 0  

The resultant binary numbers are 0100100001111101 and 0100100100000000, corresponding to 18557 and 18688, respectively, leading to pulse commands

```
pulse(1u; F1Freq(setup; 18557))
pulse(1u; F1Freq(setup; 18688))
pulse(1u; F1Freq(setup; FUD))  // ,or F1Freq(setup; 32768)
```

##### Setting the base frequency and delta frequency, and implementing frequency sweep
To be specific, let us suppose that we are going to sweep the frequency from 100.845 MHz down to 100.645 MHz with a step of -40 Hz. We define the following frequency variables in the preamble:
```
freq XFR0 = 100.645;
freq XFR1 = 100.845;
freq XDF =  -4e-5;  // deltaF in MHz
```

In addition, we have the following entries in the preamble:
```
int AD9858_2GHz_DISABLE = 16472 (1 GHz clock for DDS);
int FUD = 32768 (Frequency UpDate);
int FREQ_SWEEP_ENABLE = 16768;
int AUTO_CLR_FREQ_ACCUM = 17024;
```
The meanings of these integers have been explained above, except for the last one (`AUTO_CLR_FREQ_ACCUM=17024`). This flag is used to clear the frequency accumulator (upon reception of the FUD signal). The number 17024 came from the binary expression of the register map, in which the 7th bit is activated in address 0x02, together with the “WR” flag.

In the main part of the pulse program, frequency sweep is implemented by
```
{--- Frequency sweep start ---
pulse(500n; F1Freq(XFR1))  {   -- 1 --
pulse(500n; F1Freq(-1;XDF))  { -- 2 --  sets the freq increment (in MHz)
pulse(100n; F1Freq(setup; AUTO_CLR_FREQ_ACCUM))   { -- 3 --
                        { reset frequency to FR1
                        { This line should be followed by "FUD" (see the next line)
  pulse(100n; F1Freq(setup; FUD)) {  -- 4 --  Freq. sweep starts.  
```
First, the base frequency is set to XFR1=100.845 MHz. Here, the AD9858 chip should start operation at the specified frequency XFR1 + offset (defined in the gate definition file). In the next line, the frequency increment is set to XDF = -4E-5MHz = -40 Hz. The following “AUTO_CLR_FREQ_ACCUM” signal forces the frequency accumulator inside AD9858 to zero, immediately going to the base frequency upon reception of the “FUD” command.

To stop the frequency sweep and settle at, say, XFR0,
```
{--- Frequency sweep stop ---
  pulse(500n; F1Freq(XFR0))
  pulse(500n; F1Freq(-1;0.0))
  pulse(100n; F1Freq(setup; AUTO_CLR_FREQ_ACCUM))
  pulse(100n; F1Freq(setup; FUD))
```  

The commands presented in this section should be regarded as parts of pulse programs that have been described for the explanation purpose.

<!--
In the next section, we show an example of a whole pulse program (using the frequency sweep function) that can actually be compiled and implemented.
-->

[Back to Top](../../index.md)

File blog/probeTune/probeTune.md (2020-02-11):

{% include head.html %}
# Probe tuning using an Opencore NMR spectrometer

28 Jan 2019 Kazuyuki Takeda
- - -
## Related Topics
- [Frequency control](../dds2/dds2.md)  

## Introduction

The purpose of NMR probe tuning is to establish impedance matching at the frequency of interest. A vector network analyzer is a very useful device for tuning the probe, it may not be available. Here, we show an example of probe tuning using an Opencore NMR spectrometer. Here, we assume you have already prepared (in addition to the spectrometer):  

- a probe, or any other devices that you want to test.  
- a coupler, or a power splitter. If you want to tune the probe by monitoring the reflection of the relatively strong, power-amplified rf signals, a coaxial line section with a pickup-port, like the ones shown below, can work.
2b

The idea is to generate an rf pulse *with its frequency swept over*, send it to the probe, and measure the signal reflected back from the probe. One may adjust the trimmer capacitors in such a way that the amplitude of the reflected signal becomes minimum at the frequency of interest.

- - -

## Setup
- Load an appropriate job for probe tuning.  

- In the *Variables* tab on the **Experimental Settings** window, you can see the center frequency and the span of the frequency over which you want to measure.  
- The main part of the pulse program looks like: 
Here, the frequency at channel #1 (F1Freq) is swept by the `sweep` and `endSweep` commands. That is, during any commands sandwiched by `sweep` and `endSweep`, the frequency is swept. The start and stop frequencies are indicated by the two arguments of the sweep command. Here, we use the center frequency $f_{\mathrm{center}}$ and the span $f_{\mathrm{span}}$, so that the start frequency $f_{\mathrm{start}}$ and the stop frequency $f_{\mathrm{stop}}$ are given by

$$ f_{\mathrm{start}} = f_{\mathrm{center}} - \frac{1}{2} f_{\mathrm{span}}, $$

and

$$ f_{\mathrm{stop}} = f_{\mathrm{center}} + \frac{1}{2} f_{\mathrm{span}}. $$

Detailed description of frequency sweeping will be described elsewhere.  

- When you run, e.g., repeat scan, you get signal reflected back from your probe as a function of the frequency. An example of screenshots is shown below.
- A little trick on customizing the format of the horizontal axis may be useful. By default, the x axis represents time. On *X Axis* tab of the **Experimental Settings** panel, you can change the format by selecting *customize x axis*, and edit the initial value, increment, and so on. 
The variables declared in the current pulse program can be used. In this example, the initial value should be `fCenter-fSpan/2.0`, the increment be `fSpan/al` (`al` represents *a*quisition *l*ength). 



- You may want to view the data in various formats. It may be useful to split the plotters.  Here, I split the plotter with four views. ***Top left***: in-phase, quadrature, and absolute signals are displayed. ***Top right***: only the absolute value is displayed, and the data is magnified by limiting the plot range. ***Bottom left***: a polar plot, which is somewhat reminiscent (but *not identical*) to a Smith chart. At least you can tell the critical coupling condition in which the reflection should be minimal so that the marker at the frequency of interest get to the center of the circle. I find this option is extremely useful!. ***Bottom right***: A magnified view of the polar plot, which is also useful to make sure that the impedance matching (and therefore minimum reflection) is established.

***Enjoy!***

- - -

probeTune_ch1.ppg
```
version=2.00;
uses = defaultGates.gate;
transform F1Freq=#+180;

CLK=160;

freq fCenter=74.656;
freq fSpan=5;

amp a=5;

const int AD9858_2GHz_DISABLE=16472;

aux PD=0.1s(Pulse delay);
aux NA=100(Total scans);
aux ND=4(Dummy scans);
aux DW=10u(Dwell time);
aux AL=1024(Acq. length);

phaselist pl=(ch1; x,-x);
acqphase=x,-x;

// Any command before "start" should finish with a semicolon (;).

start   //--- Implementation begins with a "start" command. ---

  pulse(50n; F1FreqRST)
  pulse(50n; F1Freq(setup; AD9858_2GHz_DISABLE))
  delay(10m)
  pulse(5000n; F1Freq(fCenter))
  delay(1m)

Init
  pulse(1m;   RG)
  sweep(F1Freq(fCenter-fSpan/2,fCenter+fSpan/2))
  pulse(50n; ST, RG)
  pulse(dw*al; F1Amp(a), pl, F1_Gate, F1_Unblank, RG)  
  endSweep(F1Freq)
  delay(10m)
relax   

```

probuTune_ch1.nmrjob
```
[Acquisition]
FFTCheckBox=false
QDCheckBox=true
digitalFilterCheckBox=true
inFPGAAccumCheckBox=false
inFPGAAccumSpinBox=1
multipleAcquisitionCheckBox=false
multipleAcquisitionComboBox=0
multipleAcquisitionSpinBox=1
offsetCorrectionCheckBox=false
offsetCorrectionSpinBox=0
phaseReverseCheckBox=false
phaseRotationCheckBox=false
phaseRotationSpinBox=0
replaceRealWithAbsCheckBox=false
separateDataStorageCheckBox=false
separateDataStorageSpinBox=2

[Array]
arrayCheckBox=false
arrayVariables=@Invalid()
dimensions=0

[File]
commentTextEdit=
nameLineEdit=probeTune_ch1
numberOfImportedFiles=0
obsFreqCheckBox=true
obsFreqComboBox=0
obsFreqLineEdit=74.656
ppgFilename=probeTune_ch1.ppg

[Variables]
AL=1024
DW=10
NA=100
ND=4
PD=0.1
a=5
fCenter=74.656000000000006
fSpan=5
names=fCenter, fSpan, a, PD, NA, ND, DW, AL

[xAxis]
customAxisRadioButton=true
defaultAxisRadioButton=false
metricPrefixCombobox=10
unitSymbolLineEdit=MHz
xAxisLabelLineEdit=Frequency
xIncrementLineEdit=fSpan/al
xInitialValueLineEdit=fCenter-fSpan/2
```

[Back to Top](../../index.md)

<!---
, resulting in the minimized reflection of the signal.
プローブチューニングを行う目的は、観測周波数においてインピーダンスを整合させて信号の反射強度を最小にすることにある。整合（マッチングマッチング）時には、ラジオ波信号の照射効率とともにNMR信号の検出効率も最適になる。
　ここではOpencore NMR(2)を用いたプローブチューニングの例を示す。
-->

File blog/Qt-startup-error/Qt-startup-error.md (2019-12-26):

# Qt startup error (Linux)
26 Dec 2019 Kazuyuki Takeda

- - -

- On somewhat obsolete linux (CentOS), I encountered an error when I tried to launch opencoreNMR-Process-2.0.1-20191122-linux.AppImage:  
```symbol lookup error: /tmp/.mount_opencoo80U8p/plugins/platforms/../../lib/libQt5XcbQpa.so.5: undefined symbol: FT_Get_Font_Format```

- It was remedied by  
```sudo yum update freetype-devel```

- - -
[back](../../index.md)

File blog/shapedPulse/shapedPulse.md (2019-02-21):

# Shaped pulses
28 Jan Kazuyuki Takeda

- - -
### Summary
A convenient way of programming a shaped pulse is

```
pulse[n](width; strings containing one or more ‘#’ characters)
```

This is equivalent to:

```
pulse(width/n; …)  (‘#’ replaced by ‘0’)
pulse(width/n; …)  (‘#’ replaced by ‘1’)
pulse(width/n; …)  (‘#’ replaced by ‘2’)
...
pulse(width/n; …)  (‘#’ replaced by ‘n-1’)
```

### Related Topics
- [kinds of gates](../kindsOfGates/kindsOfGates.md).

### The principle of generating shaped pulses
A shaped pulse has a waveform with an amplitude-modulated profile. In addition, you may want to modulate the phase of the pulse simultaneously. A straightforward way of programming a shaped pulse is to iterate pulse commands with intended  amplitudes and/or phases incremented in discrete steps, as shown in the following example:

```
pulse(1u; F1Amp(10.0))
pulse(1u; F1Amp(20.0))
pulse(1u; F1Amp(30.0))
pulse(1u; F1Amp(40.0))
pulse(1u; F1Amp(50.0))
```

To modulate the phase as well, you may just add phase descriptions.

```
pulse(1u; F1Amp(10.0), F1Phase(1.2))
pulse(1u; F1Amp(20.0), F1Phase(2.3))
pulse(1u; F1Amp(30.0), F1Phase(3.4))
pulse(1u; F1Amp(40.0), F1Phase(4.5))
pulse(1u; F1Amp(50.0), F1Phase(5.6))
```

As you may realize, the code has a lot of similar pulse commands. The software offers several ways to simplify this process. In Opencore NMR 2, the same shaped pulse can be programmed in a single line, as shown here.

```
pulse[5](5u;F1Amp(10.0*(#+1)), F1Phase(1.2+#*1.1))
```

The software interprets `[5]` just after `pulse` to be the number of discrete steps the line splits into. The indivudual step of the shaped pulse has a width of (5 us)/5=1 us, and "#" will be replaced by 0, 1, 2, 3, 4, respectively. Opencore NMR 2 offers flexible options for writing the pulse programs. For example, the above commands can also be written as

```
pulse[5](5*1u;F1Amp(10.0*(#+1)), F1Phase(1.2+#*1.1))
```

If you want to check how the actual pulse varies with the number of steps, you may be interested in defining an integer variable in the preample of the pulse program, like,

```
int n=5;
```

and write in the main part as

```
pulse[n](n*1u;F1Amp(10.0*(#+1)), F1Phase(1.2+#*1.1))
```

Then, you can modify variable `n` later on, and even *array* it. In this example, the length of the pulse increases with `n`. If you want fix the length of the pulse to, e.g., 1 us, and just modify the number of divisions,

```
pulse[n](1u;F1Amp(10.0*(#+1)), F1Phase(1.2+#*1.1))
```

It would be perfectly fine to use a time variable in the shaped pulse:

```
pulse[n](pw;F1Amp(10.0*(#+1)), F1Phase(1.2+#*1.1))
```

where we assume that the variable `pw` is defined in the preample, like

```
time pw=1u;
```

### A sinc pulse
A sinc pulse is often utilized for band-selective excitation. For example, if you want to make a pulse of the shape of a sinc function with 11 steps, the following command will do.

```
pulse[11](pw;F1Amp(a*abs(sinc(#-5))), F1Phase(180/3.141592*atan2(0,sinc(#-5))), <and any other gates that you want to activate> )
```
Here, you need to modify both the amplitude and phase, as the sinc function can take positive as well as negative values, and only positive values are allowed for the amplitude. To implement *negative* amplitudes, you need to invert the phase.

For this purpose, `F1IQ` gate is extremely useful. The identical sinc pulse can be generated just by

```
pulse[11](pw;F1IQ(a*sinc(#-5),0), <and any other gates that you want to activate> )
```

The F1IQ gate is categorized into ***RFIQ gates***, which is described in [kinds of gates](../kindsOfGates/kindsOfGates.md).

### An arbitrary shaped pulse
The shape that you want to program may not be represented by functions. You can set a numerical shape table, like:

```
pulse[4](pw;F1Amp(table(12.3,45.6,78.9,99)))
```

This is equivalent to

```
pulse(pw/4; F1Amp(12.3))
pulse(pw/4; F1Amp(45.6))
pulse(pw/4; F1Amp(78.9))
pulse(pw/4; F1Amp(99))
```

Alternatively, you can indicate a text file located in the same directory as that of the source pulse program file.

```
pulse[4](pw;F1Amp(myTable.dat))
```

In this case, you are supposed to prepare a text file named `myTable.dat` in the same directory. The data should be separated by either comma or space (return). That is, all examples shown below should work.

```
12.3 45.6 78.9 99
```

```
12.3, 45.6, 78.9, 99
```

```
12.3
45.6
78.9
99
```

***Enjoy shaped pulsing!***

[Back to Top](../../index.md)

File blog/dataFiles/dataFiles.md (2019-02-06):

# Data Files
29 Jan 2019 Kazuyuki Takeda
- - -
### Related Topics
- Array Experiments (TODO...)

### Introduction
Here I discuss the format of the data acquired with Opencore NMR 2. At the time of writing this topic, files with the following extensions are created:

extension  | description  | notes
--|---|--
.opd  | double-precision data (binary)  | little endian
.opp  | parameters associated with .opd (text)  |  
.sm2d  | single-precision data (binary)  | little endian
.sm2p  | parameters associated with .sm2p (text)  |  
.opa  | ascii data | optional |

### Double-precision data (.opd and .opp)
- The extensions `opp` and `opd` were named after **op**encore **d**ata and **op**encore **p**arameter.
- A `.opp` file is a text file and can be viewed (and even edited at your own responsibility) with a text editor. The content looks like:

```
point=1024
dw=10
sf1=74.656
#
[Log]
actualNA=100
...
```

- Most important parameters in the `.opp` file is `point`, which carries the number of points, or often called the aquisition length (al), of a single FID data.  
- In the .opd file, the data are saved in **double-precision** and **little-endian byte-order** the following way:

```
QDataStream out(&file);
out.setFloatingPointPrecision(QDataStream::DoublePrecision);
out.setByteOrder(QDataStream::LittleEndian);

for(int m=0; m<al(); m++) out << real->sig.at(m) << imag->sig.at(m);

file.close();
```

- Here, `al()` stands for the number of points, `real->sig.at(m)` is the in-phase (or real) part of the m-th point, `imag->sig.at(m)` is the quadrature (or imaginary) part of the m-th point.
- That is, the in-phase and quadrature parts of the complex data are stored *one after another*, starting from the first (0-th) to the last points.
- If you perform an array experiment and store the data, the arrayed data will be ***appended*** to the identical `.opd` file.

##### dwell time (dw), and carrier frequency (sf1)
- The dwell time `dw` (i.e., sampling-time interval) is supposed to be given in microseconds. This information is of course necessary if you want to plot the data as a function of time. In addition, when you perform Fourier transformation, the width of the resultant spectrum will be given by the inverse of the dwell time.
- The carrier frequency, `sf1`, **given in MHz**, does not have any effect in the time-domain plot. Even in the Fourier-transformed spectrum, `sf1` does not do anything as long as the horizontal axis in represented by frequency (Hz, kHz, MHz, etc.). However, in many cases NMR spectra are plotted in *ppm* (part per million), where we definitely need information the frequency that corresponds to 1 ppm. This very information matches with the carrier frequency represented in terms of MHz, and is specified by `sf1`.
- In general, the software has no means of knowing the carrier frequency, so that the users have to judge it and tell the software. By default, the software ***assumes*** that the frequency variable declared first in the current pulse program is the carrier frequency. If this is what you intend, you do not have to do anything. If this is not the case, however, you will have to tell the software the carrier frequency.


### Single-precision data (.sm2d and .sm2p)
- The format is almost identical to the double-precision data (.opd and .opp) described above. The only difference is that the binary data is stored with *single precision*. The byte order is the same, i.e., little endian. For a single (i.e., non-arrayed) data, the points are stored in the following way:

```
QDataStream out(&file);
out.setFloatingPointPrecision(QDataStream::SinglePrecision);
out.setByteOrder(QDataStream::LittleEndian);

for(int m=0; m<al(); m++) out << (float) real->sig.at(m)
                              << (float) imag->sig.at(m);

file.close();
```

- Again, if you perform an array experiment and store the data, the arrayed data will be ***appended*** to the identical `.sm2d` file.

### .opa
- Named after **op**encore **a**scii format.  
- This is an optional file format in which the text data are saved to a file.
- This option is activated when you check the save ascii checkbox.

- Shown below is a cropped code for creating the `.opa`  file for arrayed data, whence I hope you can tell that in-phase and quadrature data of each point are written in a single line separated by a whitespace, and then line feed follows and the next point is processed. As this is a text file, I hope you can verify the format using a text editor.

```
QFile file(fn);
if (!file.open(flag | QIODevice::Text))
{
     errorMessage=QString(Q_FUNC_INFO)+ ": Failed to open " + fn;
     return false;
}

QTextStream out(&file);

for(int i=0; i<FID.size(); i++)
{
    for(int k=0; k<FID.at(i)->al(); k++)
    {
       out << QString::number(FID.at(i)->real->sig.at(k),'g',12)
           << " "
           << QString::number(FID.at(i)->imag->sig.at(k),'g',12)
           << "\n";
    } // k
    out << "\n";
} // i
file.close();
```

- Note that the size of the file can be very big when you try to store data with a long array.

### Saving data halfway through accumulation
- When the accumulation (sometimes called signal averaging) has been complete, the files of the above data are automatically created. But you may want to save data and check it *halfway through* experiments, i.e., even before the accumulation has been complete.
- During accumulation, `Save Data` button should be enabled. Just click it to save data. In this case, the files with names with a suffix "_unfinished" are created.


### Temporary data files during array increments
When each step of an array experiment has been finished, the data is appended to temporary files with a name with "_array" suffix. You may hopefully find these "_array" files useful, when you want to check the data of already finished array steps. When the whole array experiment has been complete, the "_array" files are deleted.

### Data files created/removed on repeated experiments
- If one experiment has been complete, and then you run the experiments again *without changing any experimental parameters*, the latest data are saved in files with a suffix "_1". That is, the data of the previous accumulations are retained. If you do it again and again (without changing any experimental parameters), then, another data file with a suffix "_2", "_3", ... are created.
- However, ***once you have changed any experimental parameter(s) and try to run another measurement,*** all your previous data in the same working directory will be deleted.
- If this is not what you want, you can just change the job name by editing the "Job name" line edit. Then, the current data will be kept safe and the next data will be saved in a new directory
.

[Back to Top](../../index.md)

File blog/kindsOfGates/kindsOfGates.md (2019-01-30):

# Kinds of gates
30 Jan 2019 revised by KT
29 Jan 2019 Kazuyuki Takeda
- - -
### Related Topics
- [gate definition](../gateDefinition/gateDefinition.md)
- [shaped pulse](../shapedPulse/shapedPulse.md)

### Introduction
Here I describe various kinds of *gate* defined in `*.gate` files. Detailed descriptions on *gate definition* is found [here](../gateDefinition/gateDefinition.md).

### Amplitude gate (kind=amplitude)
Suppose we have the following gate definition:
```
[ampWord]
channel = ...
bitlength = ...
kind = amplitude
ampWord_0 = ...
ampWord_1 = ...
...
```

Let me explain what happens when we use this gate in, say, the pulse command:
```
pulse(time; ampWord(value))
```
Here, `value` is a real number (or variable), which must be within a range from 0 to 100.0. The output value is determined according to

$$
  \mathrm{Round}\left( \frac{\mathrm{value}}{100.0} \times (2^{\mathrm{bitlength}}-1)\right)
$$

The precision of the floating-point number is arbitrary, but you have to take care of round-off by yourself. For example, in the case of `bitlength=10`, `value=10.0` would give us `102`, which corresponds to a binary expression of `0001100110`. Thus, the 1st, 2nd, 5th, and 6th bits are activated (Note that the least significant bit is defined to be the 0th bit). Similarly, `value=10.1` would result in `103`, so that the final output would be `0001100111`. However, `value=10.01` would make no difference from the result when `value=10.00`! At this moment, the compiler does not give you any warning messages regarding to round-off.

The amplitude gate may be useful when you want to specify the output level by percent of the maximum possible value. But if you do not like to care about the possible round-off errors, `kind=logic_vector`, described below, may be the choice.

### Logic-vector gates (kind=logic_vector)
```
[logicVectorWord]
channel = ...
bitlength = ...
kind = logic_vector
logicVectorWord_0 = ...
logicVectorWord_1 = ...
...
```
Let us say you want to implement
```
pulse(time; logicVectorWord(value))
```
Now, the value should be an integer number or variable ranging from $0$ to $2^{\mathrm{bitlength}}-1$.

### Logic gates (kind=logic)
This can be regarded as a special case of logic_vector with `bitlenth=1`. The gate definition looks like this:
```
[logicWord]
channel = ...
bitlength = 1
kind = logic
logicWord_0 = ...
```
Unlike other kinds of gate, the logic gate does not require argument(s), so that the usage is like the following:
```
pulse(time; logicWord)
```

Note the absence of the argument, i.e., parenthesized value, followed by `logicWord`. Since it carries only a single bit, the way of its usage is unambiguous; when it is used, the corresponding bit is activated, and vice versa.

### Integer gates (kind=integer)
This is a singed version of logic_vector. Its declaration and usage is quite similar to logic_vector:
```
[intWord]
channel = ...
bitlength = ...
kind = integer
intWord_0 = ...
intWord_1 = ...
...
```
An example of usage is:
```
pulse(time; intWord(value))
```
Now, `value` should be a signed integer value ranging from

$$
-2^{\mathrm{bitlength-1}}
$$
to
$$
2^{\mathrm{bitlength-1}}-1
$$
This may be used for, e.g., generating field-gradient pulses.

### Phase gates (kind=phase)
```
[phaseWord]
channel = ...
bitlength = ...
kind = phase
phaseWord_0 = ...
phaseWord_1 = ...
...
```
An example of usage is:
```
pulse(time; phaseWord(value))
```
This is used for rf phase control. The value should be given in *degrees* (not radians!). Any real number is acceptable, but periodicity is assumed. That is, `value=1.0`, `361.0`, `720.1`, `3600001.0`, `-359.0`, and so on, would all be equivalent. The value is brought within the range between 0 and 360, and the output result is then calculated according to
$$
  \mathrm{Round}\left( \frac{\mathrm{value}}{360.0} \times (2^{\mathrm{bitlength}}-1)\right)
$$

You should take care of possible round-off errors, just as in the case of the amplitude gate.

### RFIQ Gates (kind=rfiq)
By **IQ**, I mean **I**n-phase and **Q**uadrature components of radio-frequency (rf) signals. Sometimes you may want characterize rf signals by *complex* numbers, whereas, from hardware's viewpoint, it is straightforward to specify the amplitude and the phase of the signal. A signal with an amplitude $A$ and phase $\phi$ is characterized by a complex number with *in-phase* (real) and *quadrature* (imaginary) components $s_i,s_q$ being
$$
  s_i = A \cos\phi, \quad s_q = A \sin \phi
$$
Conversely, for a given set of the in-phase and quadrature components $s_i$ and $s_q$, the amplitude $A$ and the phase $\phi$ are represented as
$$
  A = \sqrt{s_i^2 + s_q^2}, \quad \phi=\tan^{-1}\left( \frac{s_q}{s_i} \right)
$$

With the RFIQ gate, you can link an amplitude gate and a phase gate. In `defaultGates.gate`, we have the following entries:
```
[f1iq]
kind = rfiq
channel = 1
amp = f1amp
phase = f1phase

[f2iq]
kind = rfiq
channel = 2
amp = f2amp
phase = f2phase

[f3iq]
kind = rfiq
channel = 3
amp = f3amp
phase = f3phase
```
Here, `f1iq`, representing the RFIQ gate for rf channel #1, is associated with the amplitude gate `f1amp` and the phase gate `f1phase`. In a pulse program, you can use it as follows:
```
pulse(pw; F1IQ(si,sq))
```
Then, the compiler interprets the command in such a way that the amplitude and the phase should be set at $\sqrt{s_i^2 + s_q^2}$ and $\tan^{-1}\left( s_q / s_i \right)$, respectively.

An example of applications of the RFIQ gate is found in a topic on [shaped pulses](../shapedPulse/shapedPulse.md).

### AD9858 Gates (kind=AD9858)
This is dedicated to control a direct digital synthesizer (DDS) board of the Opencore NMR spectrometer. It has a size of 40x40mm, and is equipped with a DDS chip AD9858 (Analog Devices). It is driven by a clock signal with a frequency of 1 GHz, and the frequency is controlled by the pulse programmer via a 0.5 mm pitch, 30 pin FPC cable. Roughly speaking, the maximum output frequency of a DDS is determined by ~0.4 times the clock frequency, which is ~400 MHz in the present case. But I have a feeling frequency generation up to ~420 MHz looks fine.


The AD9858 chip has a 2-bit register called “profile”. On each of the four ($2^2=4$) profiles, AD9858 can store separate output frequency, and later on, you can choose which is used (using a 2-bit logic_vector gate for profile selection). This function may be used to switch frequency from one value to another very rapidly. In addition, AD9858 is capable of sweeping the frequency. I will describe how to do it later.
<!--
but I must say that full control of this DDS board requires understanding the principle of its operation.
-->

In the definition of the AD9858 gate, let us say F1Freq, `bitlength` must be 16.
```
[F1Freq]
channel = ...
bitlength = 16
kind = AD9858
F1Freq_0 = ...
F1Freq_1 = ...
...
F1Freq_15 = ...
```
And the usage of this gate is
```
pulse(time; F1Freq(profile; value))
```
or
```
pulse(time; F1Freq(value))
```
In the former case, profile should be 0, 1, 2, or 3. In the latter case, profile=0 is assumed. That is, the latter,
```
pulse(time; F1Freq(value))
```
, is equivalent to
```
pulse(time; F1Freq(0; value))
```

##### Other "profile" options
This is extensions that I defined for pulse programming in Opencore NMR (i.e., no such description is found in the datasheet of AD9858). In most cases users do not have to take care of them.
- F1Freq(-1; value)  
This is used for delta-frequency tuning word.
- F1Freq(setup; value)
When we use a word "setup", instead of 0, 1, 2, 3, or -1, the AD9858 gate is interpreted as a logic_vector gate.

##### Offset Frequency
We may want to make an offset in the output frequency. That is, we may need to set the actual frequency to be
```
value+offset (in MHz).
```
What is the point of setting the offset? Well, in the Opencore NMR spectrometer, and in many other applications of radio-frequency engineering, a signal at one frequency is often mixed with a signal at another. In the transmitter of the Opencore NMR spectrometer, the output signal of this DDS board is mixed with a phase-controlled signal with a frequency fixed at 180 MHz. Then, the resultant frequency f of the transmitting signal is either `f=value+180 MHz`, or `f=value-180 MHz`. The choice is up to you, depending on if you want to up-convert or down-convert the frequency.
If you use up-conversion, it would be convenient to set
```
transform F1Freq=#-180;
```
in the preamble of the pulse program. Then, if you want to generate a signal at, say, 300 MHz, at the final output port of the transmitter, you may write
```
pulse(time; AD9858Word(300.0))
```
The compiler automatically calculate the frequency of the DDS output signal for you to be
```
300-180=120 MHz
```
Similarly, if you want to perform down-conversion, you may write in the gate definition file as
```
transform F1Freq=#+180;
```
Again, if the frequency of interest is, e.g., 75 MHz, you can write a command
```
pulse(time; AD9858Word(75.0))
```
And the compiler interprets the DDS frequency to be
```
75+180=255 MHz
```
In this way, an intuitive and straightforward programming of the transmitting frequency is possible, once the offset entry of the gate definition file is specified appropriately.

Considering the maximum frequency of the DDS output signal (400~420 MHz), down-conversion is appropriate for the resultant frequency of up to ~220 MHz. The higher frequencies up to ~600 MHz can be covered with up-conversion.

##### Profile Selection (PS)
For Profile Selection (PS) of AD9858, we have to prepare a two-bit logic_vector gate in the gate definition, like:
```
[F1FreqPS]
caption = AD9858 Profile Select for channel 1
channel = 1
bitLength = 2
kind = logic_vector
F1FreqPS_0 = 47
F1FreqPS_1 = 46
```
In this example, we set the gate name to be `F1FreqPS`, and the PS0 and PS1 pins of AD9858 (for more detail, see the data sheet of AD9858) are physically connected to the 47th and 46th bits of the line output of the pulse programmer of channel 1. Abrupt frequency switching may be implemented by
```
pulse(time; F1FreqPS(0))
pulse(time; F1FreqPS(1))
pulse(time; F1FreqPS(2))
pulse(time; F1FreqPS(3))
```
Here, we assume that we have already set the profiles 0, 1, 2, and 3.

Note that argument “0” of a logic_vector gate is equivalent to doing nothing. This means that frequency set on the 0-th profile continues to be active, unless you use profile selection.
```
pulse(time; AD9858Word(value1))
pulse(time; ...)
pulse(time; ...)
pulse(time; AD9858Word(value2))
...
```
In the above example, the frequency at `value1` set in the 1st line is kept until the 4th line, where another frequency `value2` is set. This way of switching frequency is straightforward, but takes a time interval of the order of a hundred nanoseconds. Compared to this, frequency switching by profile selection is very fast.

Frequency sweep, which I believe to be another topic of great interest, will be described elsewhere.

[Back to Top](../../index.md)

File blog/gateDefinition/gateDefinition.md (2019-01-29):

{% include head.html %}
# Gate Definition

29 Jan Kazuyuki Takeda

- - -
### Related Topics
- [Kinds of Gates](../kindsOfGates/kindsOfGates.md)  

### Introduction
A gate definition file is read by the pulse-program compiler upon reception of the uses command:
```
uses=<filename>;
```
In many cases, `uses=defaultGates.gate;` will do. This files are to be placed under `~/.opencorenmr/gates/` (Linux, Mac) or `C:\Users\(username)\.opencorenmr\gates` (Windows). This *default* gate-definition files, together with example pulse programs and jobs, can be downloaded from [.opencorenmr repository](https://github.com/opencorenmr/.opencorenmr).

The gate definition file carries information as to *physical* wire connection between the line output ports of the core module of the pulse programmer and the peripheral devices, which may be either inside or outside the FPGA chip. To begin with, we shall take a look at an example of gate definition for the rf amplitude of, say, the 3rd channel of the transmitter. As shown in the figure just below, let us suppose that the rf amplitude is determined by the signal output of a 10-bit DA converter. In this example, the 0th bit is connected to line 19 of the pulse programmer, the 1st bit to 20, and so on.


### Gate-definition file format
The gate definition file is a text file taking the form of a standard .ini file used in Windows. That is, the file is composed of a number of “sections”. A section begins with a name wrapped　by square brackets []. It should be followed by a number of “keys”. A key takes a form of keyname=value. In the present example of rf amplitude control, we set the section name to “f3amp”. Then, the section description looks like this:
```
[f3amp]
caption = RF amplitude for channel 3
channel = 3
bitlength = 10
kind = amplitude
f3amp_0 = 19
f3amp_1 = 20
f3amp_2 = 21
f3amp_3 = 22
f3amp_4 = 23
f3amp_5 = 24
f3amp_6 = 25
f3amp_7 = 26
f3amp_8 = 27
f3amp_9 = 28
```

The roles of the keys are summarized as follows:
- caption  
This serves for a comment, and any text is acceptable.
- channel  
The channel to which the gate is assigned. The value must be 1, 2, or 3. It is set to 3 in the above example, meaning that this gate is used for the 3rd rf channel.
- bitlength  
An integer (>0) specifying the number of bits used for this gate. The value is 10 in this example, because we want to control the 10-bit DA converter.
- kind  
Here, the value is set to “amplitude”. This key is used by the compiler to interpret the argument of the gate.
- sectionName_0 ... sectionName_(n-1)  
n is the integer specified in the bitlength key (n=10 in this example). These keys specify the physical wire connections. In this example (see figure), D0 is connected to the 19th bit of the line output of channel 3. We thus write
```
f3amp_0=19
```
Similarly, as D1 is connected to the 20th bit,
```
f3amp_1=20
```
, and so on. If you modify the hardware and thereby physical wire connections, you need to change the assignment accordingly.

The gate definition file is referred by the compiler with the “uses” command in the preamble. If the compiler detects no syntax errors, the section name can be used in the `pulse`, `wait_h`, `wait_l`, and `burst` commands, like:
```
pulse(100u; f3amp(45.6))
```
This means that the pulse programmer sets the output of the DA converter to 45.6% of its maximum for a time interval of 100 microseconds. In practice, you may want to combine a number of gates to be activated, like:
```
pulse(100u; f3amp(45.6), f3phase(ph1), F3_Gate, F3_Unblank)
```
If you set kind=amplitude, the argument should be a floating-point number between 0.0 and 100.0, or a variable carrying a number between 0 and 100. Instead, you might want to use
```
kind=logic_vector
```
In this case, the argument should be an integer number between 0 to $2^n-1$ (in the present example, 0 to 1023).

### Various *kinds* of gates
Possible options for “kind” include
```
kind=amplitude
kind=phase
kind=logic
kind=logic_vector
kind=integer
kind=AD9858
kind=rfiq
```
I will describe each elsewhere.

### Custom gate name
You may rename the section according to your own preference. If you want to use, say, `myGate` instead of `f3amp`, just replace [f3amp] by [myGate] in the gate definition file (the compiler does not care about the case, so `myGate`, `mygate`, and `MYGATE` make no difference). Do not forget to rename the `f3amp_n` lines to `myGate_n`  as well. Then, you will be able to use your own gate identifier:
```
pulse(100u; myGate(45.6))
```

- - -
[Back to top](../../index.md)

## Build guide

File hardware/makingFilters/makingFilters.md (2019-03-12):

# Making Filters

- 12 Mar 2019 Minor revision by Kazuyuki Takeda  
- 9 Mar 2019 Revised by Kazuyuki Takeda
- 26 Feb 2016 Original memo written by Kazuyuki Takeda

[Back to Top](../../index.md)

- - -
In this document I show how I make rf filters used in the Opencore NMR spectrometer.

- - -

### Introduction
A radio-frequency (rf) filter is an electronic component passing signals with rf ranging over a specific region of interest, while blocking those outside that region. In the Opencore NMR spectrometer as well as in many other electronic devices, rf filters are used for various purposes, such as
- removal of image frequencies generated by an rf mixer,  
- isolation between channels with different frequencies,  
- rejection of noises aliasing into view in analog-to-digital conversion,  
and so on. Here, I demonstrate fabrication of band-pass filters, to be placed between the FPGA mother board and the rf transmitter board of the Opencore NMR spectrometer.

### Fabrication
For this purpose, a circuit board, shown in the following picture, was made. It was cut into pieces. In this example, the longer board was used, while the shorter ones may be useful for making low-pass filters and attenuators.  
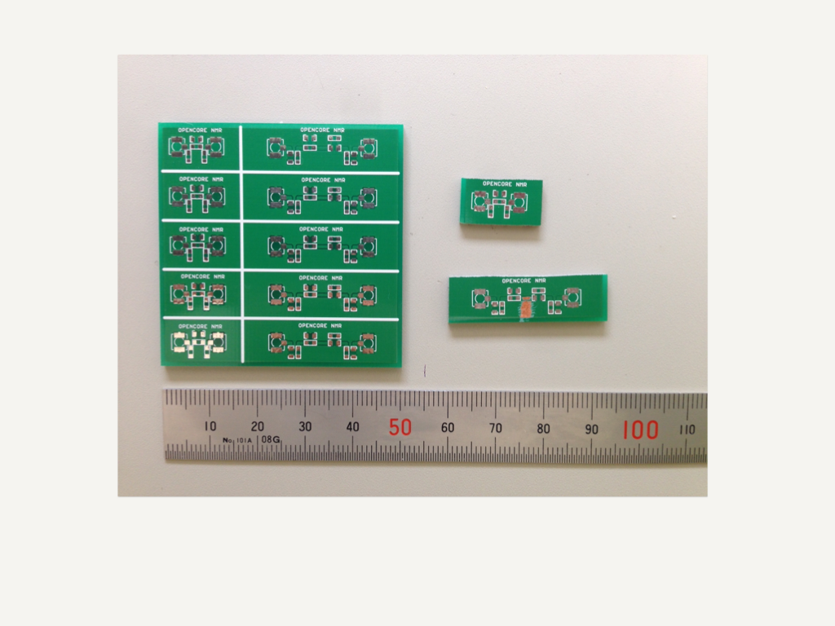
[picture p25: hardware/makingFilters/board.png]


In this example, we are interested in such a band-pass filter that passes 180 MHz and rejects 140 MHz and 300 MHz. The circuit diagram is as follows:  
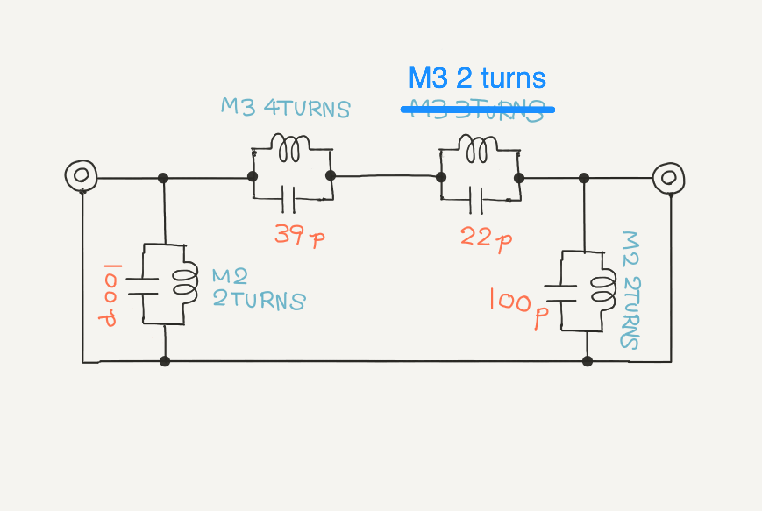
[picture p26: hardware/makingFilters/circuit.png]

Here, a description of, e.g., "M3 4 turns" means that a coil wound on a M3 screw with a number of turns of four was used. Indeed, it is convenient to use a screw to wind coils. I used a coated wire with a diameter of 0.4 mm, winding on a screw. Later on, the insulating coat was removed at the legs of the coil.  
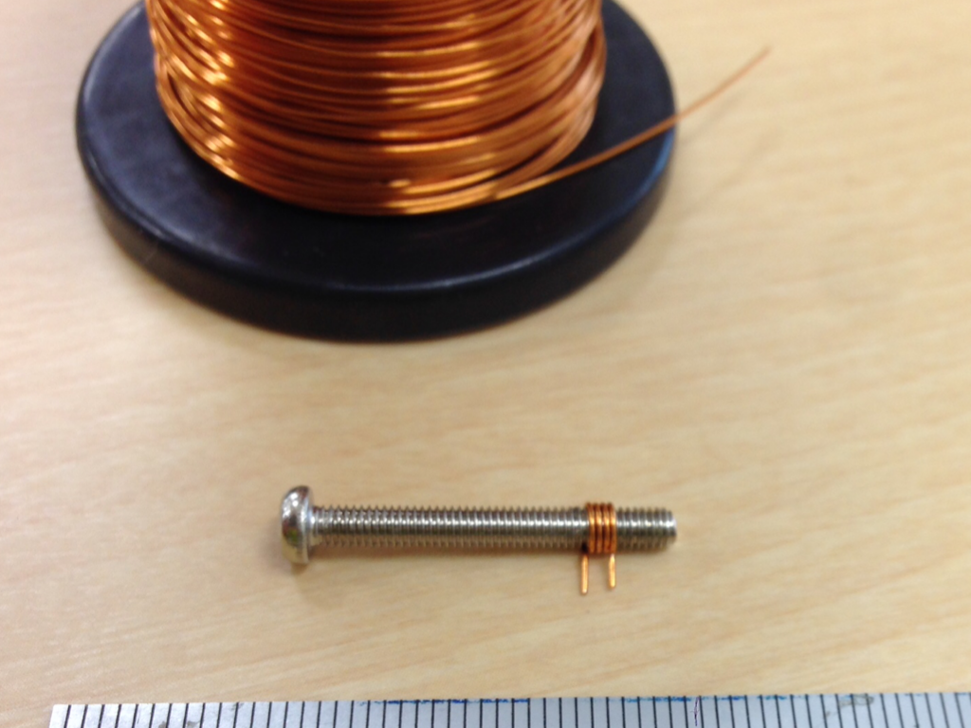
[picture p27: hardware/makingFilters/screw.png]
  

For the capacitors, I found that those of "GQM" series (Murata) work well.
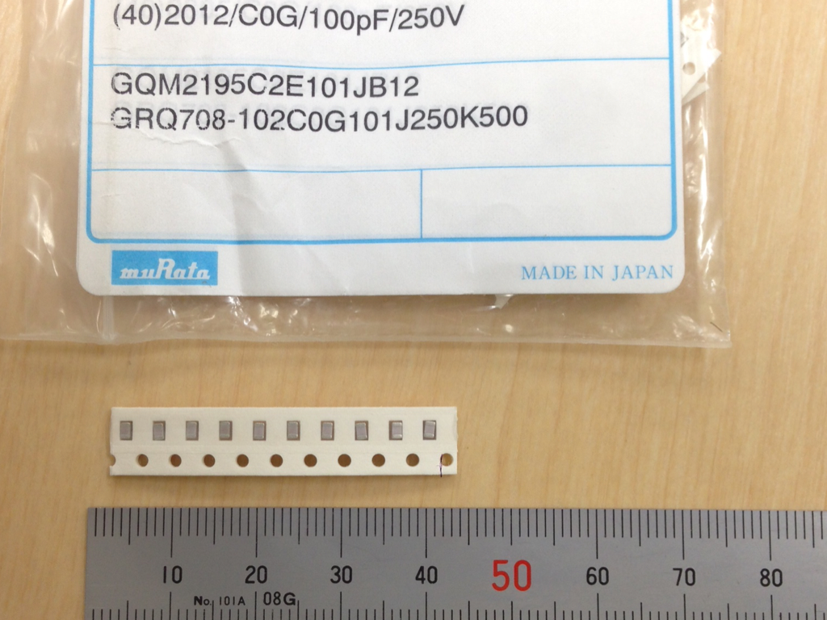
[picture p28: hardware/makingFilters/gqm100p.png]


The capacitors and the coils, as well as the surface mount coaxial connectors (U.FL series, HIROSE), were mounted on the board and soldered. Then, the coils were stretched or compressed, while the frequency response of the S21 parameter (transmission) was observed on an network analyzer, so that the insertion loss at 180 MHz was minimal, while the signals at 140 MHz and 300 MHz were reduced significantly (more than 40 dB).
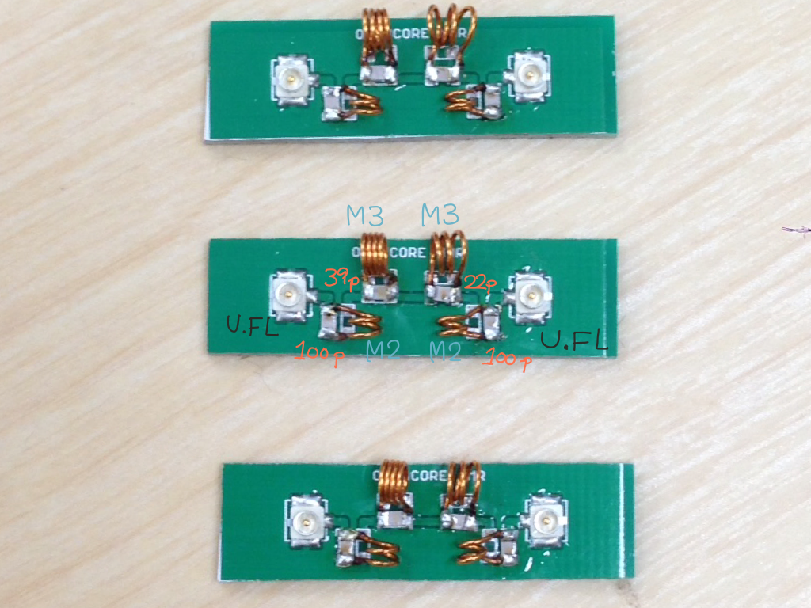
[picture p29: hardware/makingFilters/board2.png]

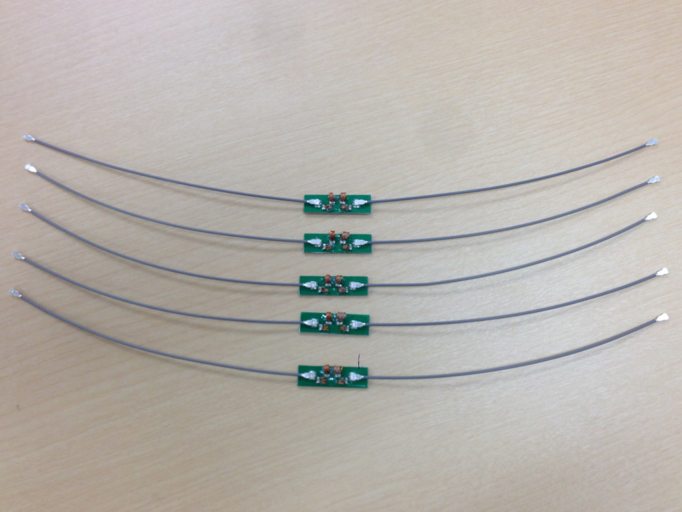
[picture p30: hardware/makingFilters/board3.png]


As shown below, the frequency response of the filter was satisfactory.


When I have made sure that the response of the circuit was good, the coils were fixed with epoxy adhesive, to prevent the coils from being deformed by external forces.
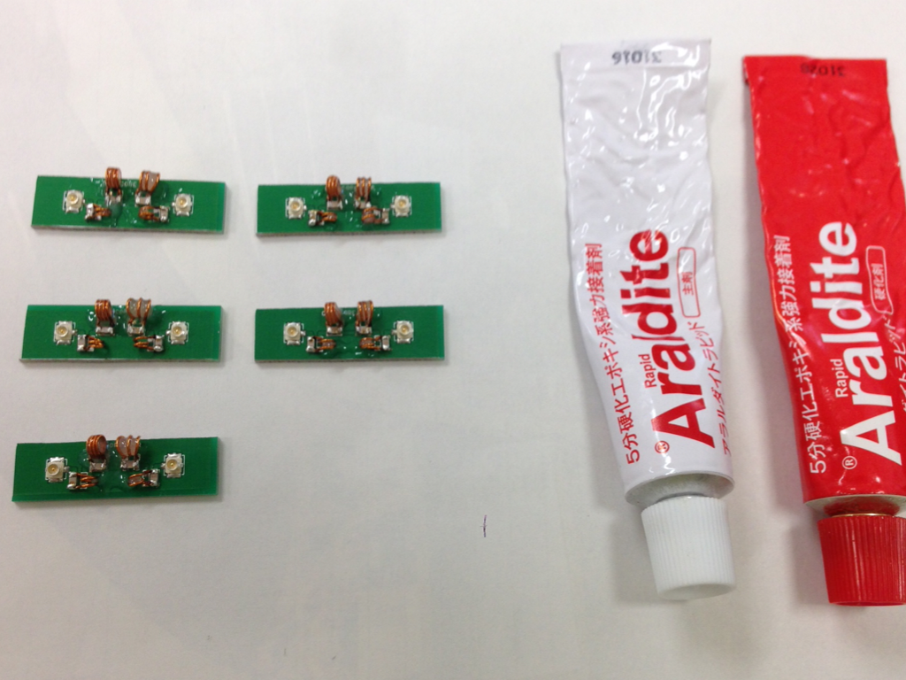
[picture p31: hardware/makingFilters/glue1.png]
  
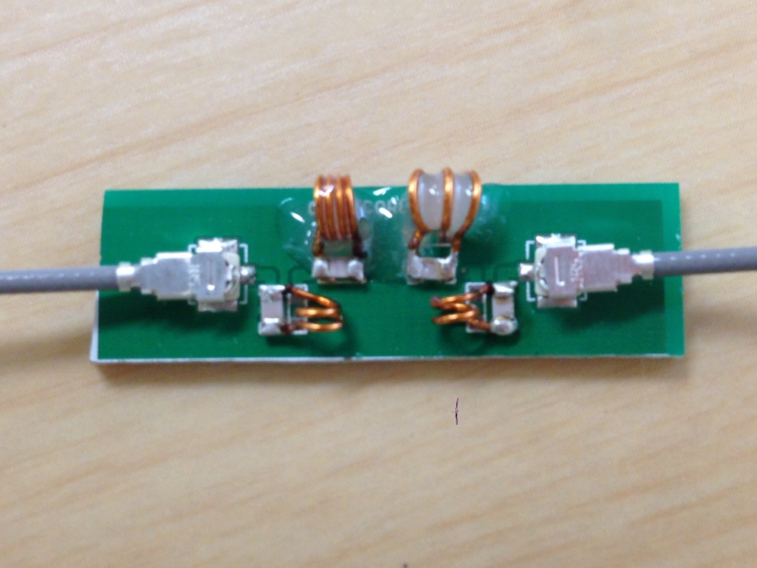
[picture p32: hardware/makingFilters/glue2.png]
  

Finally, the filters were covered with insulating hear shrinking tubes.
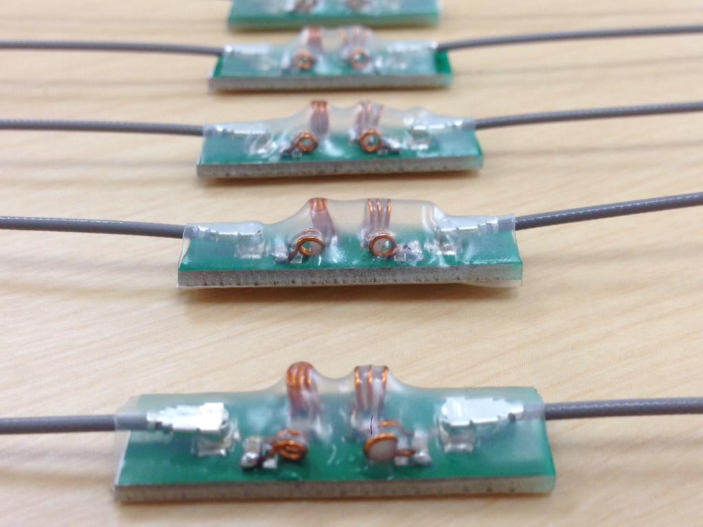
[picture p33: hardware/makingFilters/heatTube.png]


### Improvement
I found that a two-turns coil, connected in parallel with 22 pF capacitor, works better.



### Board data

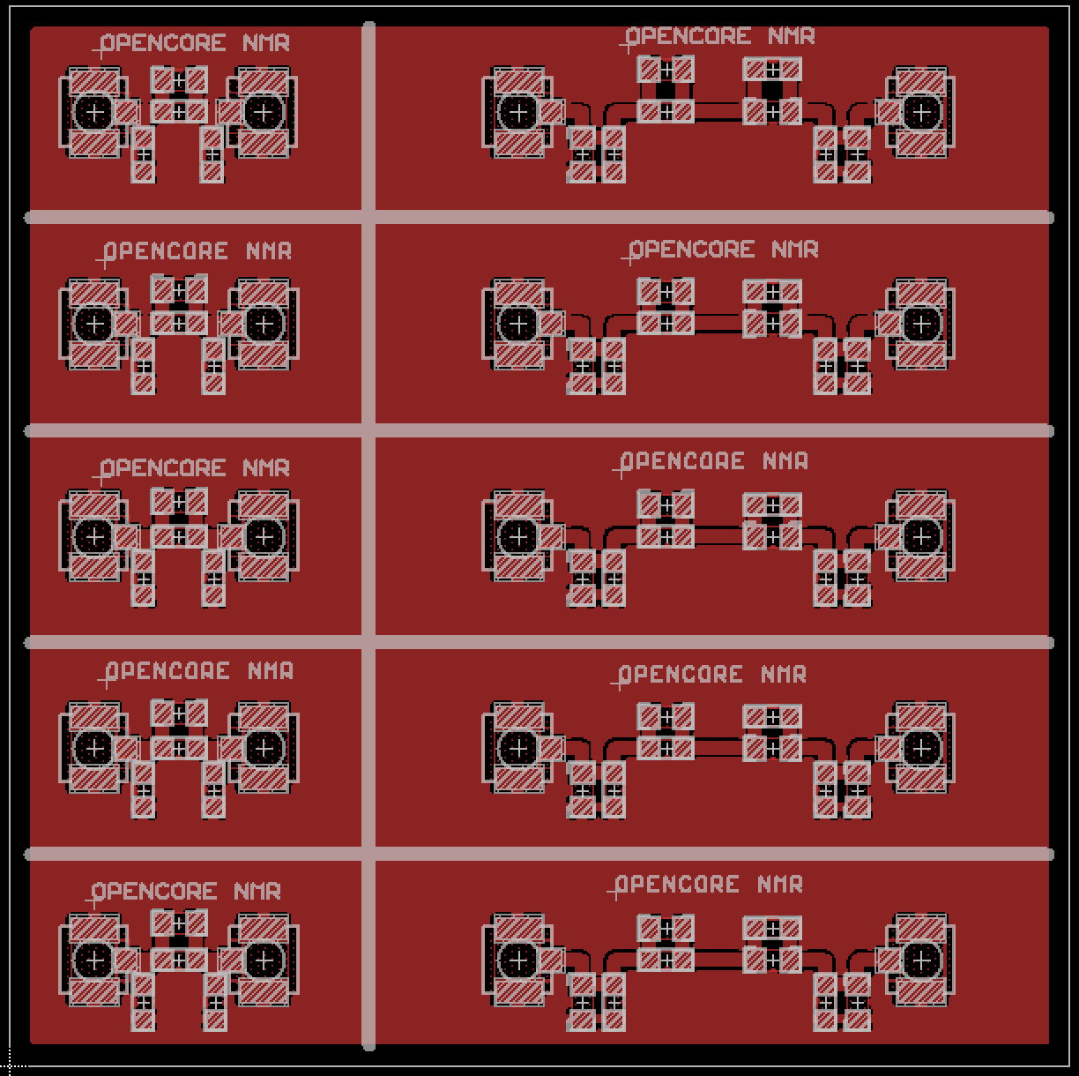
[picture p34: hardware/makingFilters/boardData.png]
  
- The board was designed on EAGLE 6.2.0 Professional  
- There is just **1 layer**, i.e., component (top) layer.  

##### EAGLE schematic and board files
- Schematic: [filters.sch](data/filters.sch)  
- Board: [filters.brd](data/filters.brd)  

##### Gerber files

- [filters.cmp](data/gerber/filters.cmp) (Component side pattern)
- [filters.plc](data/gerber/filters.plc)（Component side silkscreen)
- [filters.stc](data/gerber/filters.stc)（Component side solder resist）
- [filters.out](data/gerber/filters.out)（outline）

- - -

[Back to Top](../../index.md)

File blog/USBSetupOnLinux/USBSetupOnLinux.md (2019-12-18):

# USB setup on Linux
Correction made on 7 May 2019 by Kazuyuki Takeda  
Minor correction on 15 Oct 2018 by Kazuyuki Takeda  
Updated on 12 Oct 2018 by Kazuyuki Takeda  
Updated on 25 Aug 2018 by Kazuyuki Takeda  
Created on 26 Apr 2018 by Kazuyuki Takeda

### Installing FTDI D2XX Driver
 - Download the linux d2xx driver from [FTDI](http://www.ftdichip.com/Drivers/D2XX.htm).
 - Open a terminal and go to the directory in which you have downloaded the above driver.
 - `tar xvzf libftftd2xx-x86_64-1.4.6.tgz`.
 - Go to the `build` directory.
 - `sudo cp libftd2xx.* /usr/local/lib`.
 - `sudo chmod 0755 /usr/local/lib/libftd2xx.so.1.4.6`.
 - `sudo ln -sf /usr/local/lib/libftd2xx.so.1.4.6 /usr/local/lib/libftd2xx.so`.
 - If you need to build the opencore NMR software from source, you also need to copy the header files. Go up the directory and copy `ftd2xx.h` and `WinTypes.h` to `/usr/local/include`.
 - Whenever you plug in the USB cable, you need to run `sudo rmmod ftdi_sio`, but in the following I describe how to let the computer do it automatically on the event of plug-in.

### (new) Plug and play on Linux (16 Oct 2018)
 - Open a terminal.
 - Run `lsusb`.
 - Find the line in the message containing `Future Technology Devices International, Ltd ...`.
 - In this line there should be a label something like: `Bus 001 Device 008: ID 0403:6010` (numbers can be different).
 - Go to `/etc/udev/rules.d/`, and make a new text file with a name of, say, `opencoreNMR.rules`.
 - One easy way to do so is `sudo vi opencoreNMR.rules`. Then, write as follows:
 ```
 ACTION=="add",ATTRS{idVendor}=="0403",ATTRS{idProduct}=="6010",MODE="0666",RUN+="/sbin/rmmod ftdi_sio",OPTIONS="last_rule"
 ```
 - Be sure to use `ATTRS{idVendor}` and `ATTRS{idProduct}`. Do **not** use ATTR{idVendor} and ATTR{idProduct} (note the latter does not include "S"), otherwise I found out that `RUN+=...` does not work.
 - The points are (i) mode 666 (read and write permission for all), and (ii) implementation of `rmmod ftdi_sio`.
 - Tell the change made to the computer by: `sudo udevadm control --reload-rules && udevadm trigger`
 - Then, when the USB cable is plugged, you can have an access to the spectrometer.

### (obsolete) Non-root access to FTDI USB devices on linux
 - Open a terminal.
 - We assume that we already have disabled the default FTDI module by `sudo rmmod ftdi_sio`.
 - Run `lsusb`.
 - Find the line in the message containing `Future Technology Devices International, Ltd ...`.
 - In this line there should be a label something like: `Bus 001 Device 008: ID 0403:6010` (numbers can be different).
 - In this example, (i.e., if you got `BUS 001`), go to `/dev/bus/usb/001`, and `sudo chmod a+w ./008`.
 - Then, you should be able to implement the opencore NMR software and establish connection with the spectrometer without root privilege.

- - -

[Back](../../index.md)

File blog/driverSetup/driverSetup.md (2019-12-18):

# Driver installation
11 Jan 2019 Kazuyuki Takeda  

Here, let us take a look at how to setup the computer, regarding:
- Device driver  
- software  

We assume you already have an operational Opencore NMR hardware. We also assume that the eprom on the USB board has already been configured. For eprom configuration [see the link](../usb_eprom/mprog.md).

### Driver installation
The way that the driver is to be installed depends on the operating system (Linux, Mac, Windows).

#### Linux
Download a [D2XX driver](https://www.ftdichip.com/Drivers/D2XX.htm) from FTDI, extract the downloaded file, and follow the instruction written in ReadMe.txt. That is:
- Copy the libraries to /usr/local/lib:
`sudo cp libftd2xx.* /usr/local/lib`
- Give non-root access to the shared object:
`sudo chmod 0755 /usr/local/lib/libftd2xx.so.1.4.8`
- Create a symbolic link:
`sudo ln -sf /usr/local/lib/libftd2xx.so.1.4.8 /usr/local/lib/libftd2xx.so`

To enable plug and play feature, follow what is written in [USB Setup on Linux](../USBSetupOnLinux/USBSetupOnLinux.md).

#### Mac
Download a [D2XX driver](https://www.ftdichip.com/Drivers/D2XX.htm) from FTDI, extract the downloaded file, and follow the instruction written in ReadMe.rtf. That is, open a Terminal, and:
- Copy the dylib file to /usr/local/lib:
  `sudo cp Desktop/D2XX/libftd2xx.1.4.4.dylib /usr/local/lib/libftd2xx.1.4.4.dylib`
- Make a symbolic link:
  `sudo ln -sf /usr/local/lib/libftd2xx.1.4.4.dylib /usr/local/lib/libftd2xx.dylib`

To disable the built-in driver, you may have to run  
`sudo kextunload -bundle com.apple.driver.AppleUSBFTDI`
every time you re-connect the USB cable. Whenever this operation is necessary, the console software gives you a message to do so.

#### Windows
- If you plug in the USB cable, the operating system may automatically detect the hardware and install the right driver.  
- To verify if the driver has successfully been installed, open device manager, and see the "Universal Serial Bus controllers".  
- It will be all right if both "USB Serial Converter A" and "USB Serial Converter B" are recognized.  
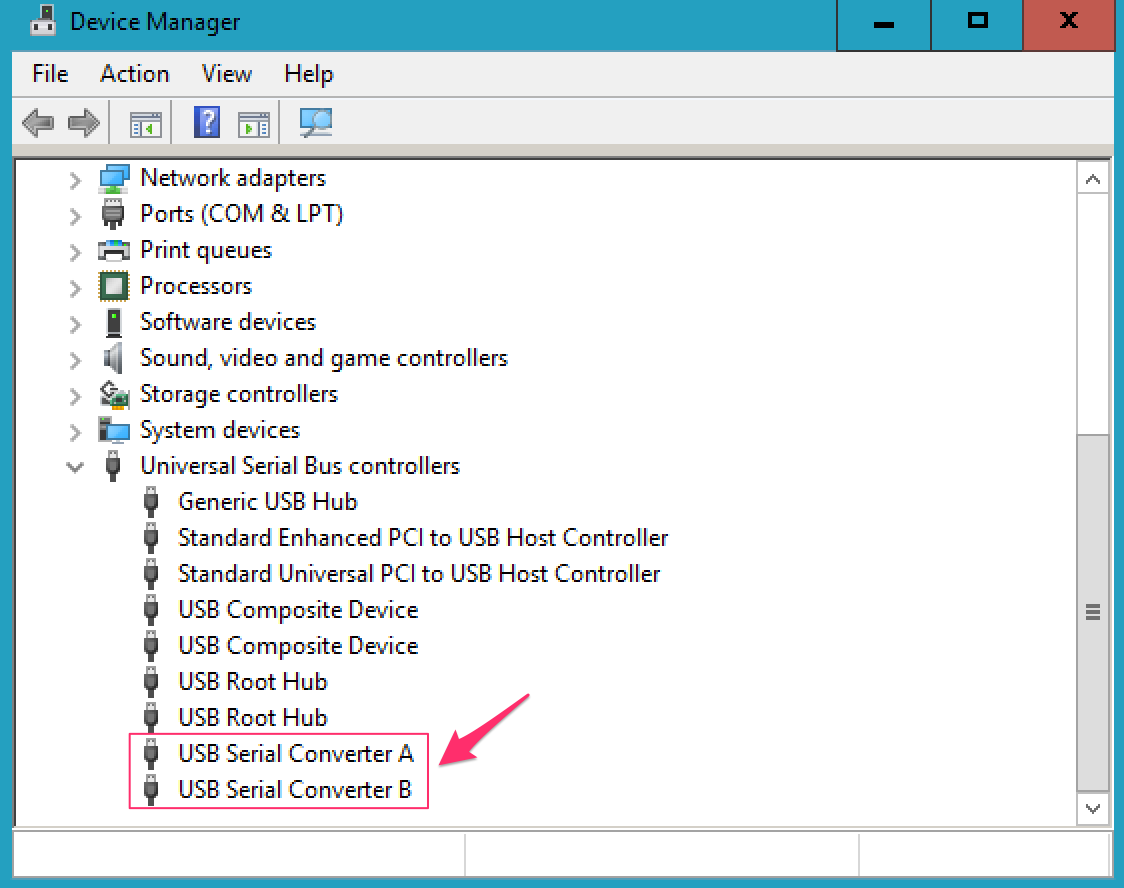
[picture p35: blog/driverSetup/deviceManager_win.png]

- If there is something wrong with the driver, you can download a [D2XX driver](https://www.ftdichip.com/Drivers/D2XX.htm) from FTDI.  

### Settings
Clone `.opencorenmr` to the home directory of your computer:
[https://github.com/opencorenmr/.opencorenmr.git](https://github.com/opencorenmr/.opencorenmr.git)

As a result, you will have .opencorenmr directory under your home directory:
- Linux: ~/.opencorenmr, or /home/(username)/.opencorenmr  
- Mac OSX: ~/.opencorenmr, or /Users/(username)/.opencorenmr  
- Windows: C:\\Users\\(username)\\.opencorenmr  

.opnecorenmr directory contains:

- `gates` directory,
- `examples` directory,

as well as `*.ini` files. In `gates` there are *.gates file, which we call ***gate definition*** files. Descriptions on the gate definiton files will be presented elsewhere.

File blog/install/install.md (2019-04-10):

# Installation of Opencore NMR2

- 10 Apr 2019 Kazuyuki Takeda  

- - -

### Linux

##### Using an .appimage
You need to:
- [install the d2xx driver](../driverSetup/driverSetup.html).  
- [setup USB](../USBSetupOnLinux/USBSetupOnLinux.md)  
- [setup `.opencorenmr`](https://github.com/opencorenmr/console-devel-2.0.1/tree/master/settings)  
- (optional) [setup GPIB](../gpibOnLinux/gpibOnLinux.md)  

##### Compilation from source
If you intend to compile from source, you need to:
- [install the d2xx driver](../driverSetup/driverSetup.html).  
- [setup USB](../USBSetupOnLinux/USBSetupOnLinux.md)  
- [setup `.opencorenmr`](https://github.com/opencorenmr/console-devel-2.0.1/tree/master/settings)  
- (mandatory) [setup GPIB](../gpibOnLinux/gpibOnLinux.md)  

In addition, you will have to:
- setup Qt  
- [compile and install LAPACK library](../lapack/lapack)  

- - -
### Mac OSX
- Under preparation...

- - -
### Windows
- Under preparation...

- - -

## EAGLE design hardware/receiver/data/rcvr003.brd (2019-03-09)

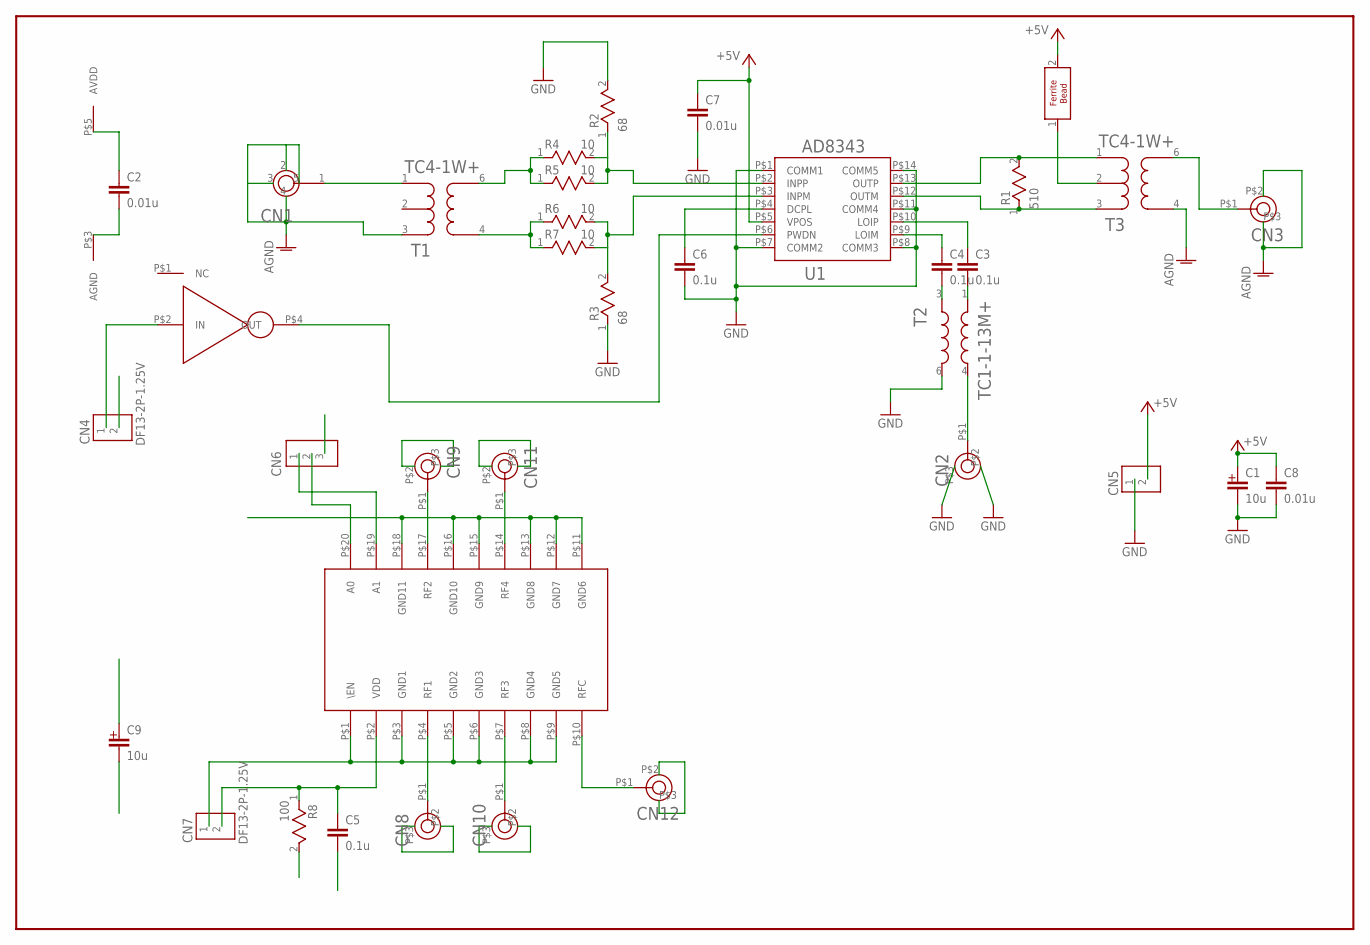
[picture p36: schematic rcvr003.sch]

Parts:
C1, C9: 10u; 3216_POLAR
C2, C7: 0.01u; 1005
C3, C4, C5, C6: 0.1u; 1005
C8: 0.01u; 1608
CN1: SMASTRAIGHT; SMA_STRAIGHT
CN2, CN3, CN8, CN9, CN10, CN11, CN12: U.FL-R-SMT
CN4, CN5, CN7: DF13-2P-1.25V; DF13-2P-12.5V
CN6: DF13-3P-1.25V
FB2: FERRITEBEAD; 1608
R1: 510; 1608
R2, R3: 68; 1608
R4, R5, R6, R7: 10; 1005
R8: 100; 1608
T1, T3: TC4-1W+; AT224
T2: TC1-1-13M+; AT224
U1: AD8343
U2: MC74VHC1G04
U3: ADG904; ADG904_TSSOP

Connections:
3.3V: C5.1, C9.1, CN7.2, R8.1, U3.P$2 (VDD)
+5V: C1.1, C2.1, C7.1, C8.1, CN5.2, FB2.2, U1.P$5 (VPOS), U2.P$5 (AVDD)
AGND: C1.2, C2.2, C6.2, C7.2, C8.2, CN1.2 (GND), CN1.3 (GND), CN1.4 (GND), CN1.5 (GND), CN2.P$2 (AGND), CN2.P$3 (AGND2), CN3.P$2 (AGND), CN3.P$3 (AGND2), CN4.2, CN5.1, R2.2, R3.1, T1.3, T2.6 (4), T3.4, U1.P$1 (COMM1), U1.P$7 (COMM2), U1.P$8 (COMM3), U1.P$11 (COMM4), U1.P$14 (COMM5), U2.P$3 (AGND)
GND2: C5.2, C9.2, CN7.1, CN8.P$2 (AGND), CN8.P$3 (AGND2), CN9.P$2 (AGND), CN9.P$3 (AGND2), CN10.P$2 (AGND), CN10.P$3 (AGND2), CN11.P$2 (AGND), CN11.P$3 (AGND2), CN12.P$2 (AGND), CN12.P$3 (AGND2), U3.P$1 (\EN), U3.P$3 (GND1), U3.P$5 (GND2), U3.P$6 (GND3), U3.P$8 (GND4), U3.P$9 (GND5), U3.P$11 (GND6), U3.P$12 (GND7), U3.P$13 (GND8), U3.P$15 (GND9), U3.P$16 (GND10), U3.P$18 (GND11)
N2: R8.2
unnamed: CN4.1, U2.P$2 (IN)
unnamed: CN12.P$1, U3.P$10 (RFC)
unnamed: CN10.P$1, U3.P$7 (RF3)
unnamed: CN8.P$1, U3.P$4 (RF1)
unnamed: CN9.P$1, U3.P$17 (RF2)
unnamed: CN11.P$1, U3.P$14 (RF4)
unnamed: CN6.2, U3.P$20 (A0)
unnamed: CN2.P$1, T2.4 (3)
unnamed: CN1.1, T1.1
unnamed: U1.P$6 (PWDN), U2.P$4 (OUT)
unnamed: CN6.1, U3.P$19 (A1)
unnamed: CN3.P$1, T3.6
unnamed: FB2.1, T3.2
unnamed: R1.2, T3.1, U1.P$13 (OUTP)
unnamed: R1.1, T3.3, U1.P$12 (OUTM)
unnamed: C6.1, U1.P$4 (DCPL)
unnamed: C4.1, U1.P$9 (LOIM)
unnamed: C3.1, U1.P$10 (LOIP)
unnamed: C4.2, T2.3 (2)
unnamed: C3.2, T2.1
unnamed: R2.1, R4.2, R5.2, U1.P$2 (INPP)
unnamed: R3.2, R6.2, R7.2, U1.P$3 (INPM)
unnamed: R4.1, R5.1, T1.6
unnamed: R6.1, R7.1, T1.4

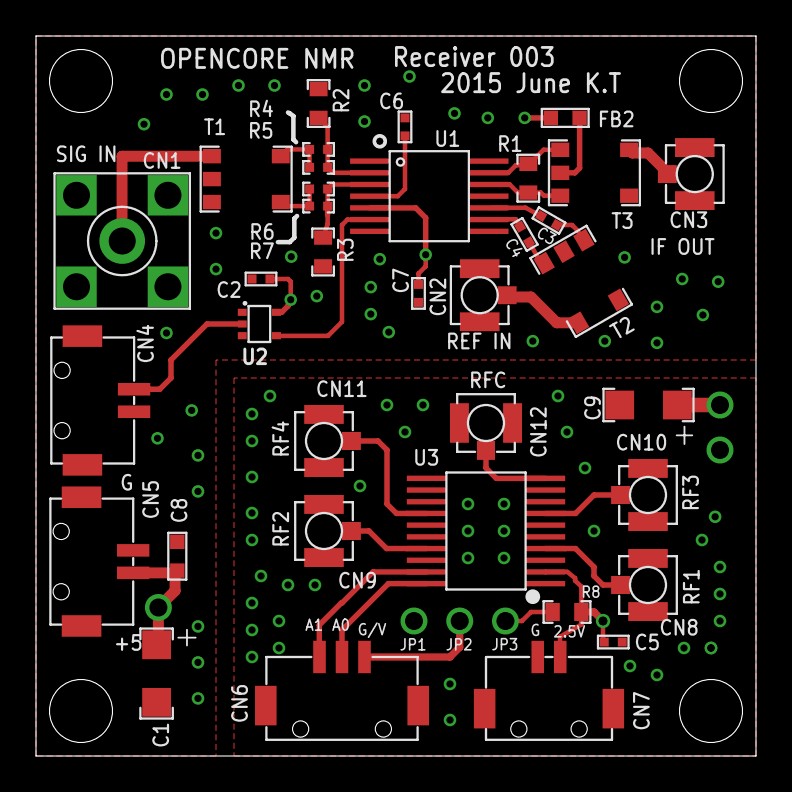
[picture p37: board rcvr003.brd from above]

Board: 4 copper layers, 40.0 x 40.0 mm, 36 parts (0 on the bottom side), 28 nets.

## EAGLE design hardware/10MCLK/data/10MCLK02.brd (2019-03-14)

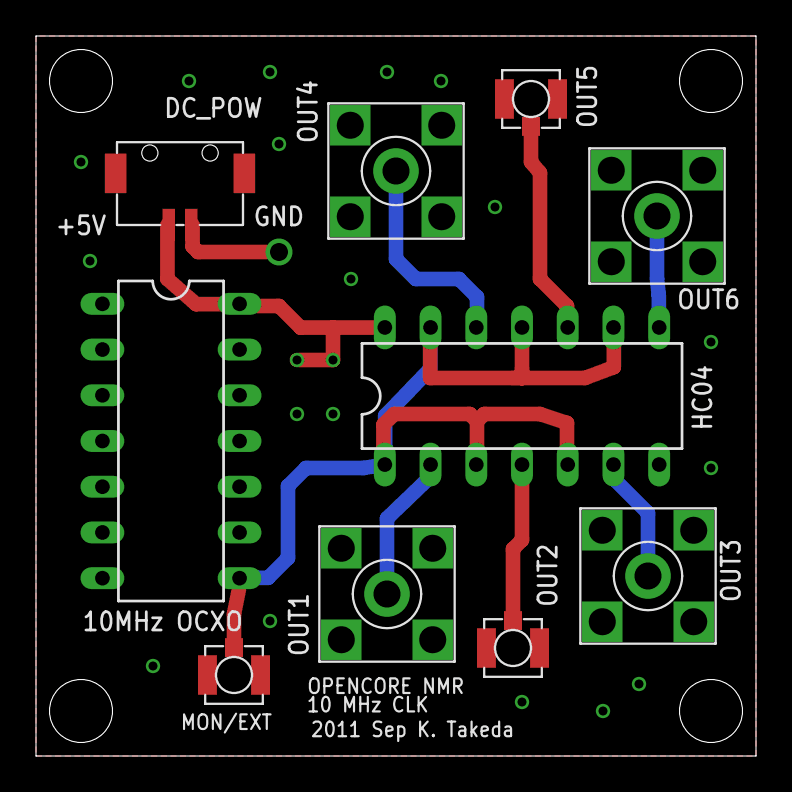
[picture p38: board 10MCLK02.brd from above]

Board: 2 copper layers, 40.0 x 40.0 mm, 10 parts (0 on the bottom side), 9 nets.

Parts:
10MCLK: DIL14
DC_POW: DF13-2P-12.5V
E$2: DIL14
E$10, E$11: U.FL-R-SMT
MON/EXT: U.FL-R-SMT
OUT1, OUT3, OUT4, OUT6: SMA_STRAIGHT

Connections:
10IN: 10MCLK.8, E$2.1, E$2.3, E$2.5, E$2.9, E$2.11, E$2.13, MON/EXT.P$1
+5V: 10MCLK.14, DC_POW.2, E$2.14
GND: 10MCLK.7, DC_POW.1, E$2.7, E$10.P$2, E$10.P$3, E$11.P$2, E$11.P$3, MON/EXT.P$2, MON/EXT.P$3, OUT1.2, OUT1.3, OUT1.4, OUT1.5, OUT3.2, OUT3.3, OUT3.4, OUT3.5, OUT4.2, OUT4.3, OUT4.4, OUT4.5, OUT6.2, OUT6.3, OUT6.4, OUT6.5
S$2: E$2.4, E$10.P$1
S$5: E$2.10, E$11.P$1
S$7: E$2.12, OUT4.1
S$8: E$2.8, OUT6.1
S$9: E$2.2, OUT1.1
S$10: E$2.6, OUT3.1

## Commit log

2019-02-23 Commit by Takeda on a local computer
    [mother-002.brd, mother-002.sch]
2023-05-10 Update receiver.md
    Link to "solder side silkscreen" was deleted (because the data did not exist from the beginning!)
